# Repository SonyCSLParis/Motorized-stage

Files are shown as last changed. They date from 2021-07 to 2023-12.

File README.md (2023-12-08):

# CSL-stage
__keywords__: Stepper motors, Arduino, Python, Freecad, 3D printing

The goal of this module is to provide simple tools to control a motor to automate manual tasks.

An Arduino is used to control the stepper motors with motor shields. The motors are controllable: 
- via Arduino through the serial interface
- with a Python library that communicates serially with the Arduino
- with a user-friendly Tkinter interface based on the Python library
  
The use of limit-switches is integrated and is preferred for safety and reproducibility. 

## Pre-requisites

- Install [CSL-Serial](https://github.com/SonyCSLParis/CSL-Serial) and the [Arduino software](https://www.arduino.cc/en/software)
- The stepper motor(s) and motor shield(s) are readily available. Refer to the example gallery for ideas. 
- The code was tested on Windows and Linux

## Hardware :gear:
Check-out the example gallery and the description of how to implement them: turning a manual stage in a motorized one, building a microscope focus module, increasing the displacement range of a piezo-motor, etc. 

| Component|      Quantity      |  Price per unit | Example|  
|----------|:-------------:|------:|------:|  
| Arduino Uno |    1   |   24€ | [Robotshop](https://www.robotshop.com/eu/fr/microcontroleur-arduino-uno-r3-usb.html)|  
|Stepper motor | tested up to 3 | |
| Stepper driver | | |
| Wires | | |

## Software :desktop_computer:

| Software | Version we used | Download |
|----------|:-------------:|:-------------:|  
| Arduino | 1.8.13 | [download](https://www.arduino.cc/en/software)
| Python  | 3.7 |[install](https://github.com/Alienor134/Teaching/blob/master/Python/Installing_Anaconda_creating_environment.md)
| CSL-serial | 1.0 | [install](XXX)

## Codes and files provided :chart_with_upwards_trend:

An [Arduino code](Oquam/Oquam.ino) is provided to control the motors. An extra layer is added in Python to conntrol it easily.
[CSLstage](CSLstage/CSLstage.py) is a class that can be used the following way:

```python
from serial import Serial
from CSLstage import ControlStage

arduino_port = "COM6"

stage = ControlStage(arduino_port, [1,1,1]) #gearbox ratio of X, Y and Z axis
stage.handle_enable(1)
stage.move_dx(10)
stage.handle_enable(0)
stage.reset() 
```

# Instructions

## Connect the Arduino, the stepper driver and the stepper motor
Refer to the docmentation of the stepper driver you selected to perform the wiring. For example: [EasyDrive stepper motor driver](https://www.instructables.com/How-to-Interface-Easy-Driver-With-Stepper-Motor-Us/), [XY-motorized stage wiring](https://github.com/SonyCSLParis/Motorized-stage/tree/main/XY-stage), 

## Arduino and Python codes  

First install Arduino IDE and Python 3.7 (links in the **Software** section)  
Second download this repository. We will call the address where you save it "path/to/repo" (for example "C://User/Me/MyRepos").

Open the [Oquam/Oquam.ino](Oquam/Oquam.ino) file. 
Open it with Arduino IDE software by double clicking on the file **Oquam.ino** and upload the codes on the Arduino by clicking on the arrow. If it fails make sure that you are correctly connected to the Arduino: check the card type and the COM port in the "Tools" ("Outils" on the image). 

<p align="center">
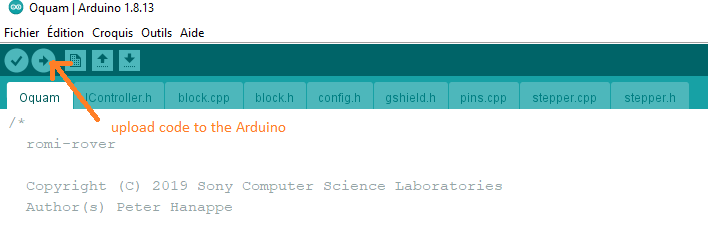
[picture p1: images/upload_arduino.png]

</p>

Note: You will have to determine the backlash of each of your motors: the number of steps you have to turn before the platform moves when you change directions. You will find 4 backlash values, one per direction per motor. We found backlash values between 7 and 12 steps. 

## Examples"

### Photos

    

### How to reproduce: 

https://github.com/SonyCSLParis/Motorized-stage/tree/main/XY-stage  
https://github.com/SonyCSLParis/Motorized-stage/tree/main/Z-stage  
https://github.com/openUC2/UC2-Motorized-XY-Table  

## License

This project is licensed under the [GNU General Public License v3.0](https://tldrlegal.com/license/gnu-general-public-license-v3-(gpl-3))

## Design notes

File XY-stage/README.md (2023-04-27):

# Automation of a manual microscope stage
__keywords__: Stepper motors, Arduino, Python, Freecad, 3D printing

The goal of this project is to convert a manual microscope stage into a motorized one.   
We control the motorized stage via Python and provide a user-friendly interface as well as the 3D models for the parts we replaced.
The precision of displacement approaches the micrometer.   
We added precisions for the budget. The maximum budget if you buy the manual stage and go through a supplier for the 3D-printing is 500€.

<p align="center">
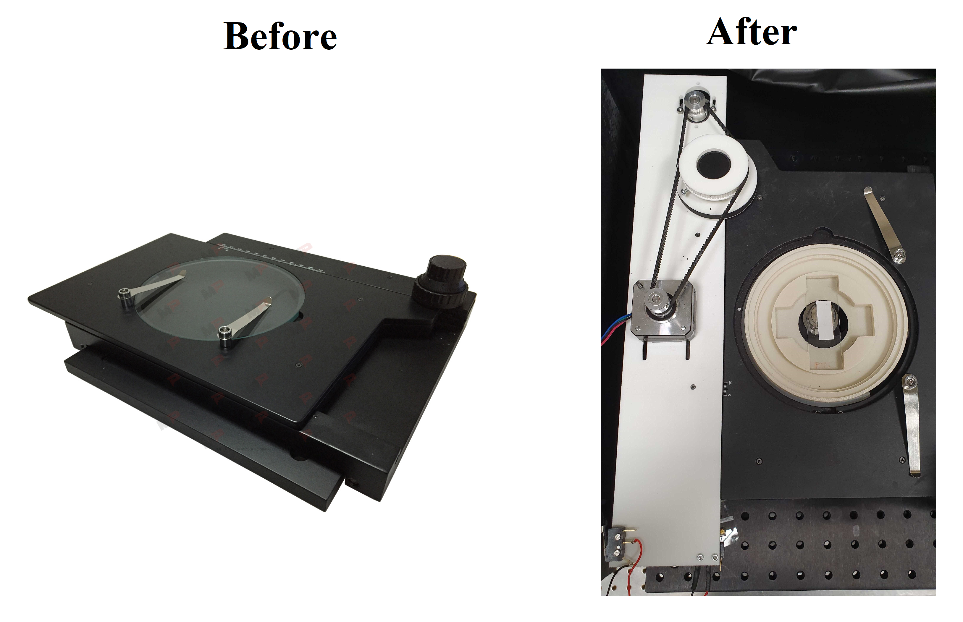
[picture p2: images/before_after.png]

</p>

# Method

The knobs initially used to manually move the platform are linked to motors via 2 belt-pulley systems (X and Y displacements). One removable part of the platform is replaced by a 3D-printed part that allows to fix the two motors. The pulleys are also 3D-printed to fit on the knobs. 

An Arduino is used to control the two stepper motors with two motor shields. The motors are controllable
-  via Arduino through the serial interface
- with a Python library that communicates serially with the Arduino
- with a user-friendly Tkinter interface based on the Python library

# Bill of materials

## Hardware :gear:
We used what we had in our drawers, it may be possible to reduce the costs by changing some of the equipment. 

| Component|      Quantity      |  Price per unit | Example|  
|----------|:-------------:|------:|------:|  
| Manual XY stage |  1 | 245€ | [Amazon](https://www.manualpositioning.com/e_products_show/?id=45)|  
| Arduino Uno |    1   |   24€ | [Robotshop](https://www.robotshop.com/eu/fr/microcontroleur-arduino-uno-r3-usb.html)|  
| Stepper driver | 2 |    10€ | [Robotshop](https://www.robotshop.com/eu/fr/controleur-moteur-pas-easydriver.html?gclid=EAIaIQobChMIhLiChaj58QIVxQwGAB1bUgYvEAQYASABEgIi8vD_BwE) |  
| Stepper motor  (0.9 °/s, 11 N/cm)  |1 | 11€ | [17HM08-1204S](https://www.omc-stepperonline.com/fr/nema-17-bipolaire-0-9deg-11ncm-15-6oz-in-1-2a-3-6v-42x42x21mm-4-fils.html)|  
| Stepper motor with gearbox| 1| 73€ |[42STH38-100](https://www.gotronic.fr/art-moteur-42sth38-100-18839.htm)|  
| Motor belt GT2 |2 |1€|[Phidgets](https://www.phidgets.com/?tier=2&catid=42&pcid=35) |
| Motor pulley 20 teeth/5mm bore |2 | 1€ |[Phidgets](https://www.phidgets.com/?tier=2&catid=42&pcid=35) | |
| Connection wires | | |  
| Screws M2, M3 | | |  
| 3D printer |

Websites where you can buy the hardware: Motedis, Phidgets, Robotshop, rs-online, RepRap

If you don't own a 3D printer you can use the platform [Sculpteo](https://www.sculpteo.com). Average delivery time: 2 weeks, possibility to pay for faster delivery. [Example of order](images/sculpteo_order.png).

## Software :desktop_computer:
Only open-source softwares

| Software | Version we used | Download |
|----------|:-------------:|:-------------:|  
| Freecad | 0.19 |  [download](https://wiki.freecadweb.org/Download)
| Arduino | 1.8.13 | [download](https://www.arduino.cc/en/software)
| Python  | 3.7 |[install](https://github.com/Alienor134/Teaching/blob/master/Python/Installing_Anaconda_creating_environment.md)

## Codes and files provided :chart_with_upwards_trend:

### 3D designs: 
- [scalable pulley Freecad](3D_models/large_button.FCStd) (modified from [manueaswn's scalable pulley](https://www.thingiverse.com/thing:3875983) )
- [small button pulley](3D_models/large_button_100t.stl)  
- [large button pulley](3D_models/medium_button_80t.stl)
- [plate element](3D_models/plaque_moteur_gearbox.stl)

### Control of motors by Arduino 
- [libromi](https://github.com/romi/libromi/tree/c6992f0516e695cd28e09cd8dcbb921d4bc2097d) (written for the [Romi Project](https://github.com/romi/libromi))
- [interface](codes/launch_interface.py)

# Results

In the end we were able to control the movement of the stage to go from one trap to the following one. The following animation shows a trap and its neighbour appearing one after the other in the center of the camera.

<p align="center">

</p>

<p align="center">
Credits: Léa Pinon and Jacques Fattacioli for the microfluidic set-up (ENS, IPGG), Thomas Le Saux and Aliénor Lahlou for the imaging set-up (ENS, Sony CSL)
</p>  

By using the EasyDriver we could rotate each motor by one microstep. In the end the set-up enabled us to reach a minimal movement of 1,95 μm along the **x** axis and of 0,05 μm along the **y** axis.

In order to estimate the quality of our set-up, we measured its precision using the registration method which calculates the spatial correlation between two successive images.

On the one hand the analyses of these results shows that the stage moves linearly along the **y** axis as expected. We concluded that our set-up was of good quality for this direction.

<p align="center">
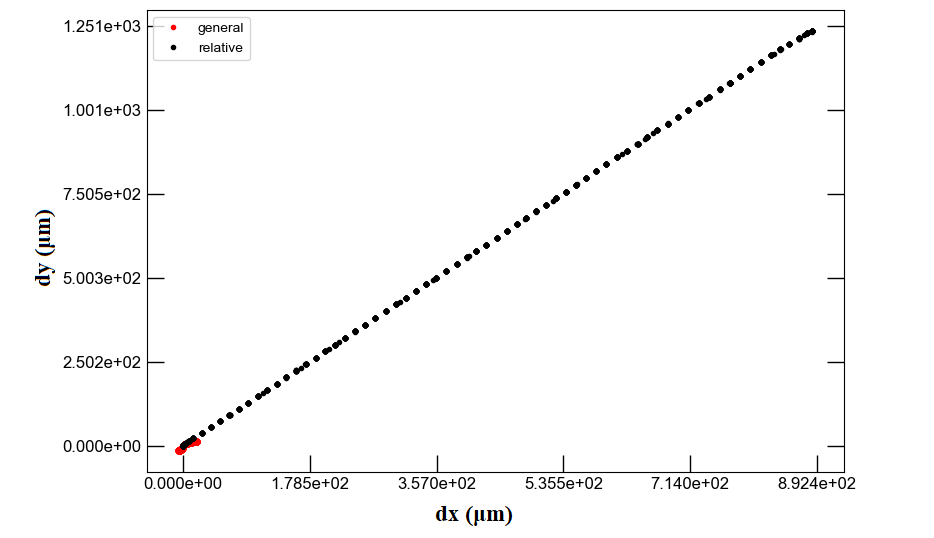
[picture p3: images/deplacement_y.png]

</p>

On the other hand we discovered that the movement along the **x** axis is flawed. Indeed when moving the stage along this axis we regularly measure a small unwanted movement along the **y** axis. This shortcoming leads to imprecise movement along the **x** axis, and it seems to come from the mechanics of the manual platform.

<p align="center">
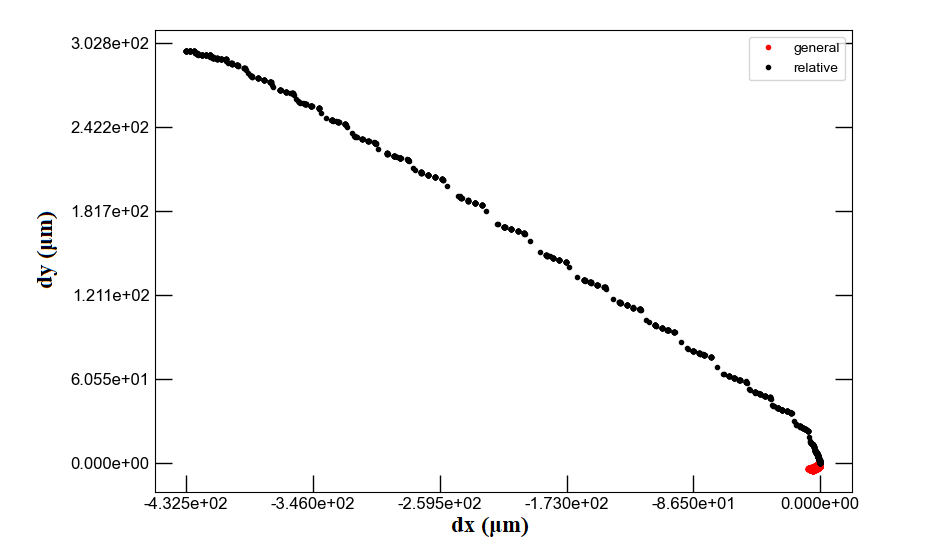
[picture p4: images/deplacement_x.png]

</p>

For the **x**-axis we measured that one turn of the knob moves the stage by 2,5 cm. In the case of the **x** axis the 17HM08-1204S stepper motor has 3200 microsteps per revolution and the master pulley has 20 teeth. Thus we calculated that the **x**-axis slave pulley needed to have 32 teeth. Such a little number of teeth leads to modeling issues.

Thus we decided to design an 80 teeth slave pulley for the **x**-axis knob. This leads to a higher precision : when the stepper motor rotates by 1 microstep, the stage moves by 1,95 μm along the **x** axis (with a simple Nema 17 motor)

### New plate

Because of structural constraints, the stepper motors had to be fixed to the stage. This is why we decided to replace a plate screwed upon the stage by a new one whose 3D template we created by using FreeCAD.

This new plate has attachment points for both stepper motors and for potential switches and can be screwed to the stage.

<p align="center">
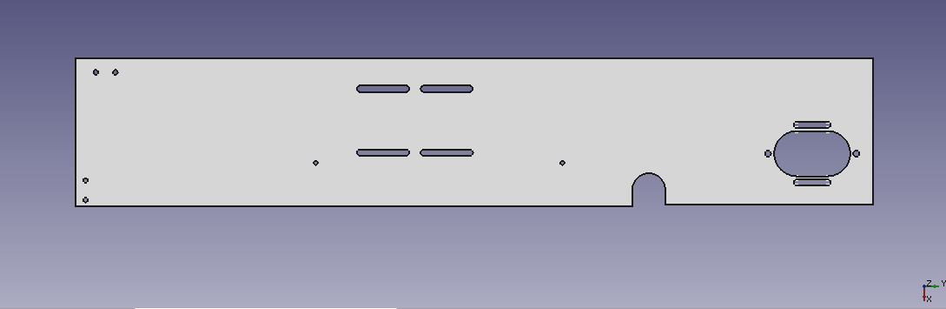
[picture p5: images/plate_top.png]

</p>  

## Assembly

In order to keep things simple we decided to control both stepper motors with one Arduino UNO microcontroller. We still had to use one EasyDriver microcontroller for each stepper motor. We used [Brian Schmalzhaus' example](https://www.schmalzhaus.com/EasyDriver/Examples/EasyDriverExamples.html) running multiple stepper motors. The set-up can be seen in the following diagram. As we wanted precise movements, we enabled microstepping control for both motors by adding connections between the MS1 and MS2 pins and the ground for each EasyDriver microcontroller.

<p align="center">
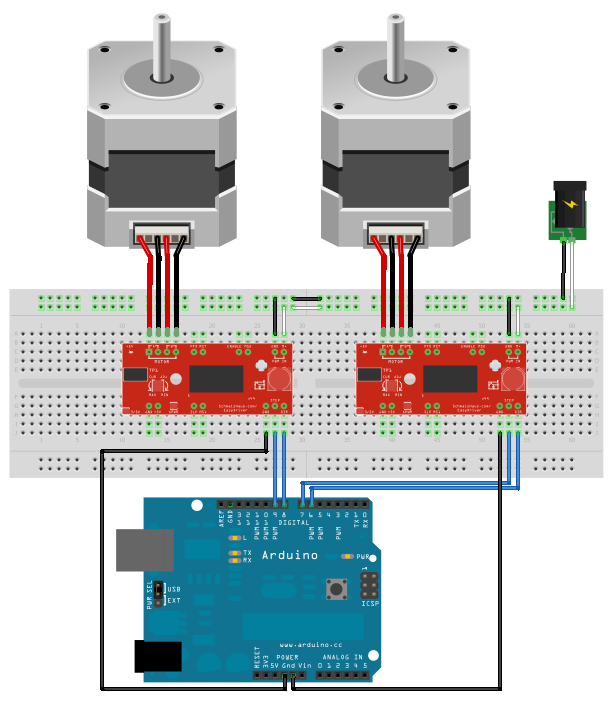
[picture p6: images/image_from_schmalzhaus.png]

</p>

To make the interaction user-friendly, we developed a code that sends instructions to the Arduino through the Serial port. It requires Python. If you already use Python for other projects, you will want to keep this code isolated from your current install. This is possible with a virtual environment. Open Anaconda Prompt and navigate to the repository

```
conda env create -f environment.yml
```
Now activate the environment:  

```
conda activate motorized-stage
``` 

You can launch the interface 

```
cd path/to/repo (here replace by your own path)
cd XY-stage/codes
python launch_interface.py
```
Press the buttons to move by predefined values, or enter manually a value and press the "move" button. The values correspond to motor steps.

<p align="center">
<img src="../images/command_interface.png" width=400"/>
</p>

Note: You will have to determine the backlash of each of your motors: the number of steps you have to turn before the platform moves when you change directions. You will find 4 backlash values, one per direction per motor. We found backlash values between 7 and 12 steps. 

## Thanks

We thank Peter Hanappe for the advices on the mechanical parts and for providing codes to control the motors. We thank Eric Aït-Yahiatène for the 3D-printing. 

## License

This project is licensed under the [GNU General Public License v3.0](https://tldrlegal.com/license/gnu-general-public-license-v3-(gpl-3))

## Contacts
If you have questions you can contact Ali Ruyer-Thompson (ali.ruyer--thompson :email: ens.psl.eu) or Aliénor Lahlou (alienor.lahlou :email: ens.psl.eu)

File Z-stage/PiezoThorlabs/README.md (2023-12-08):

# Coarse control of a piezo-controlled translation stage

Thorlabs provides a travel stage ([NFL5DP20](https://www.thorlabs.com/newgrouppage9.cfm?objectgroup_id=720&pn=NFL5DP20/M)) with a coarse manual translation range of 5 mm with possibility to 
actuate a fine transational movement with a piezo controller ([KPZ101](https://github.com/SonyCSLParis/Motorized-stage/blob/main/Z-stage/PiezoThorlabs/KPZ101.jpg)).  

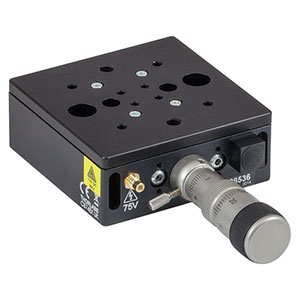
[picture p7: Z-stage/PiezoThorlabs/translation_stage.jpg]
stage

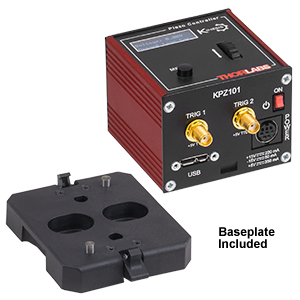
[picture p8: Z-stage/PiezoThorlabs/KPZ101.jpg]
piezo
  

The Thorabs translation stage translation movement controlled by a piezoelectric controller allows fine movements that could not be achieved with a stepper motor. However, the automated range of displacement of the stage is intrisically limited by the piezo, to 20 µm.   
We decided to automate the coarse control with a stepper motor connected to the manual differential micrometer drive via a belt-pulley system. the pulley was designed using the parametric pulley model provided [here](). We added holes to attach the piece to the differential drive part with screws.  

The part we designed has 55 teeth and can be found [here](https://github.com/SonyCSLParis/Motorized-stage/blob/main/Z-stage/PiezoThorlabs/z_focus_55_teeth_190.stl).  

setup

The design requires to adjust the position of the motor pulley to keep the belt orthogonal to the drive rotation, and to firmly attach the stepper motor to the optcal bed.   

The Nema motor is controlled by CSL-stage code, according to the descripition here: https://github.com/SonyCSLParis/Motorized-stage.

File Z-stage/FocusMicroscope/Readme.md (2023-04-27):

# 3D design for the autofocus component

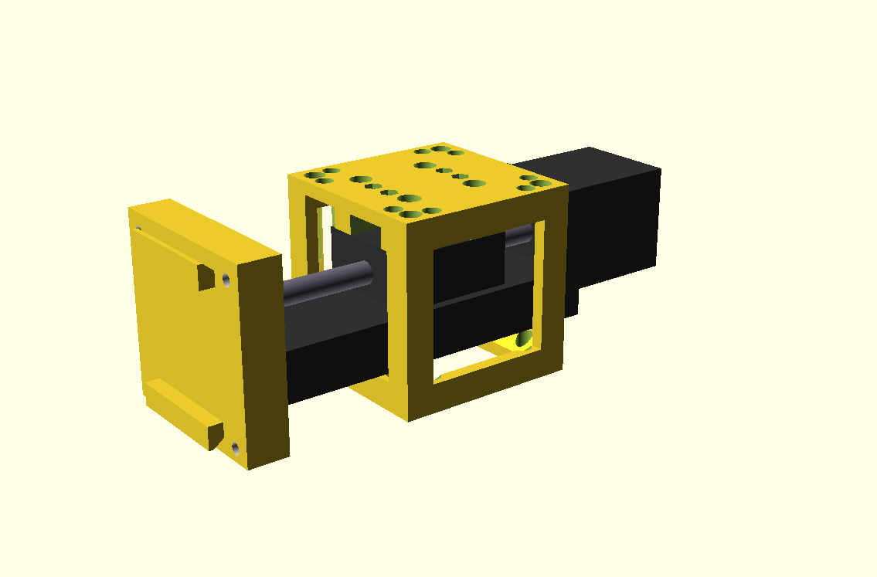
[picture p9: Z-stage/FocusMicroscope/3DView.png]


The autofocus module is based on the small linear slider found, among other, on Amazon ([French site](https://www.amazon.fr/dp/B08Y6VZMC8?ref=ppx_yo2ov_dt_b_product_details&th=1), [US site](https://www.amazon.com/s?k=Linear+Rail+50mm+nema11&crid=AHAYTX9E18IR&sprefix=linear+rail+50mm+nema%2Caps%2C635&ref=nb_sb_noss)).

On the front side, the sample holder snaps onto the front panel of the slider thanks to four spheric magnets. The sample itself is held using a simple rubber band.

The module includes two limit switches to detect the start and end position of the linear slider. The switches are the [Omron D2F-01L-D3](https://omronfs.omron.com/en_US/ecb/products/pdf/en-d2f.pdf).

The current 3D design was made with [OpenScad](https://openscad.org/).

The main files are:

* FocusMicroscope.scad: The main file that bundles the different components together.
* Structure.scad: The components of the focus module.
* LinearSlider.scad: 3D model of the linear slider.
* UC2.scad: A 3D model of the UC2 cube.

## Bill of materials

| Quantity | Description |
|----------|-------------|
| 1 | [Linear slider](https://www.amazon.com/s?k=Linear+Rail+50mm+nema11&crid=AHAYTX9E18IR&sprefix=linear+rail+50mm+nema%2Caps%2C635&ref=nb_sb_noss) (50 mm or 100 mm, NEMA11 stepper motor) |
| 2 | M2 x xx mm screws  |
| 2 | M2 nuts |
| 4 | M3 x xx mm screws |
| 2 | M3 x xx mm screws |
| 4 | Spheric magnets, 5 mm |
| 2 | [Omron D2F-01L-D3](https://omronfs.omron.com/en_US/ecb/products/pdf/en-d2f.pdf) |
| - | Wire for the limit switches |

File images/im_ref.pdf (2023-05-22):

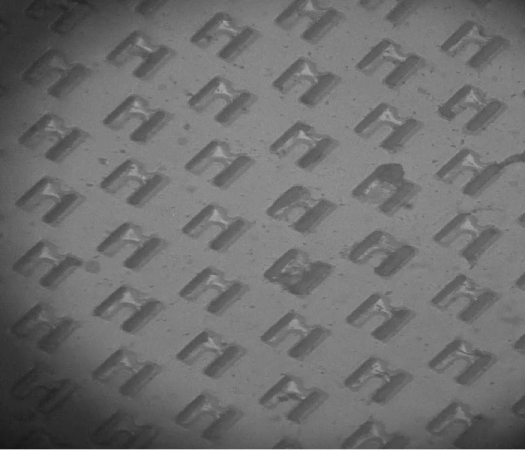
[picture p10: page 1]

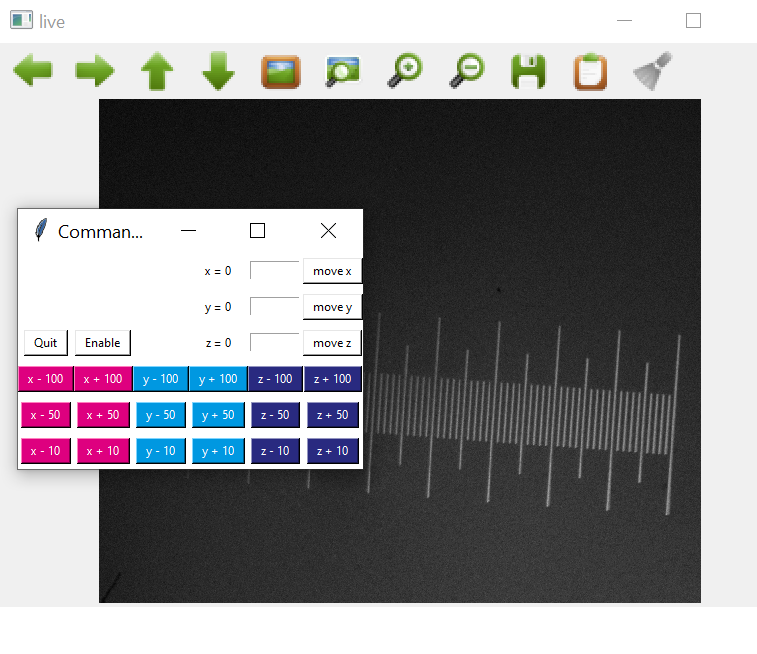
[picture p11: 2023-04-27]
images/inter_xyz.png

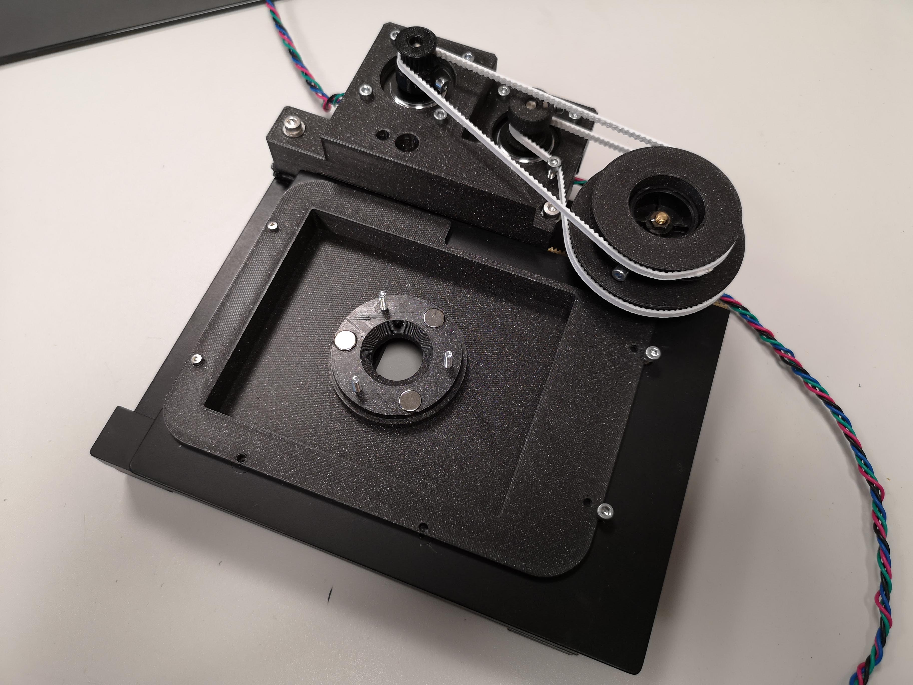
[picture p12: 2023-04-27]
images/UC2_stage.jpg

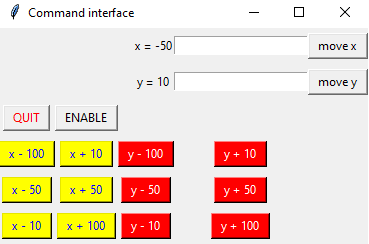
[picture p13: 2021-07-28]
images/command_interface.png

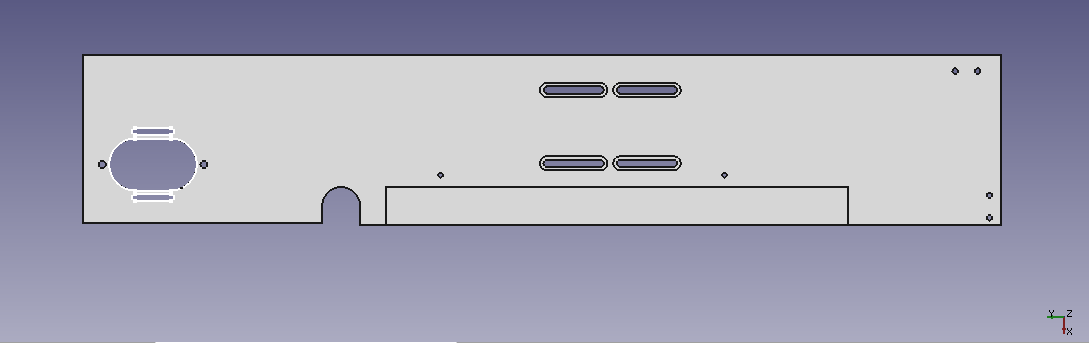
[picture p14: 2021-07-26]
images/plate_bottom.png

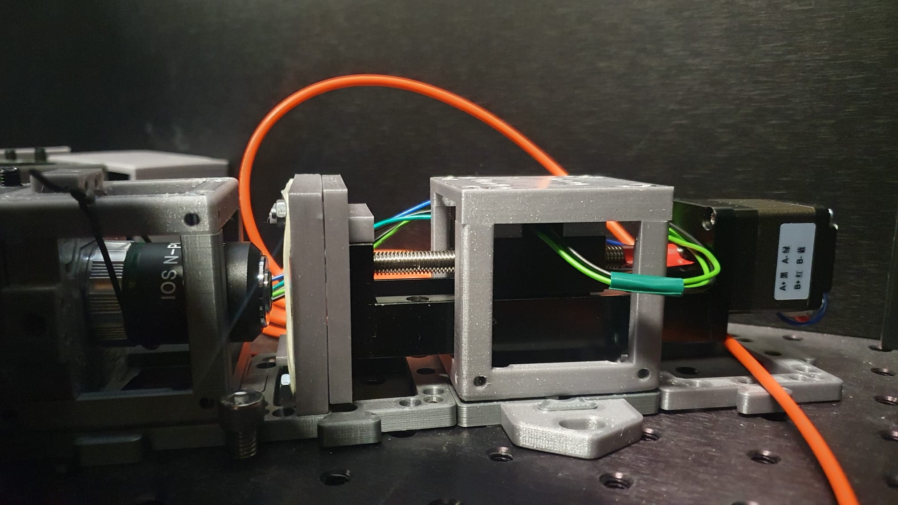
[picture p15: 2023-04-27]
images/Z_focus_UC2.jpg

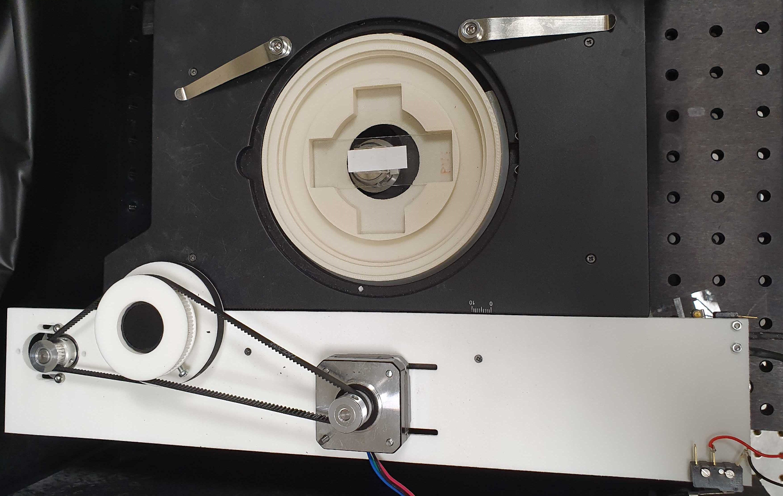
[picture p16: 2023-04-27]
images/modified_stage.jpg

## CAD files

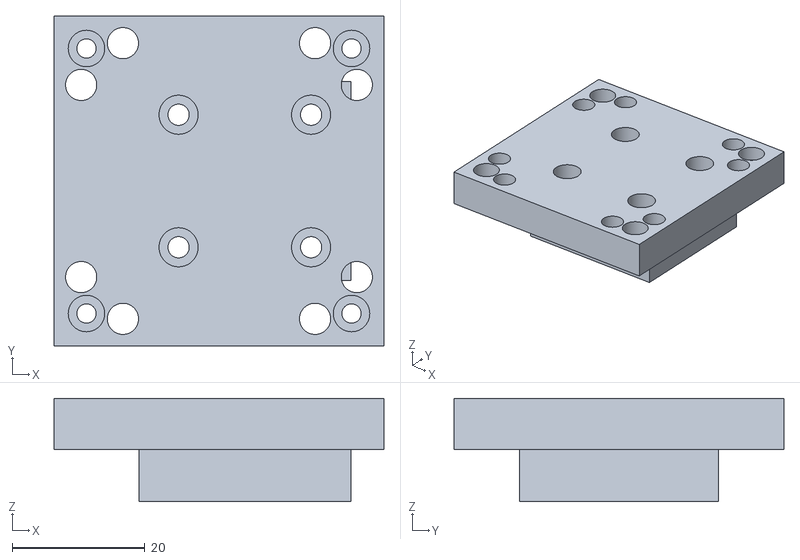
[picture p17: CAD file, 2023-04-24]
XY-stage/3D_models/FocusMicroscope_Top.stl
49.8 x 49.8 x 15.6

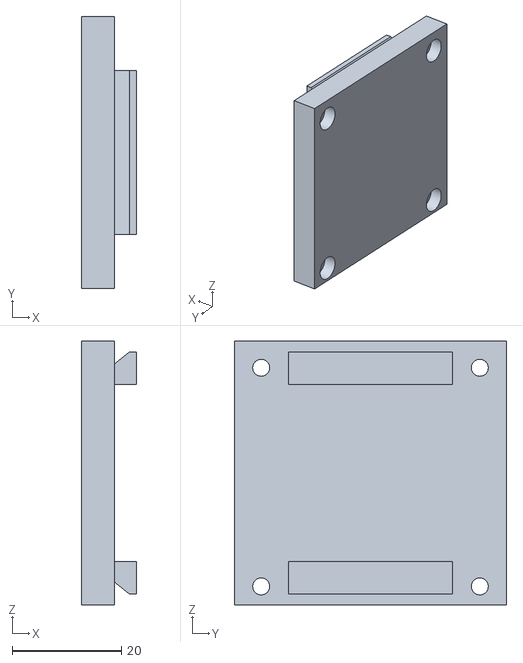
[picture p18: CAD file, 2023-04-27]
Z-stage/FocusMicroscope/SampleHolder.stl
10.0 x 49.8 x 48.3

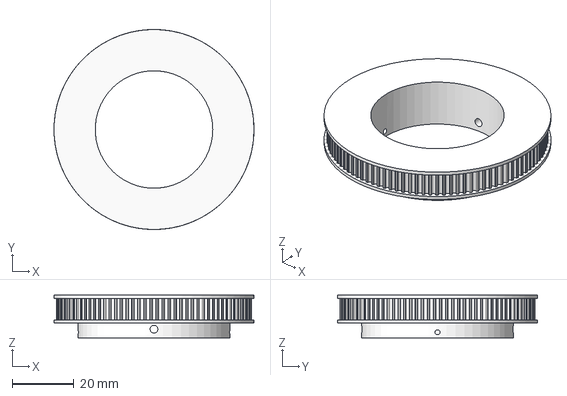
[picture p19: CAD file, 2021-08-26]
XY-stage/3D_models/large_button.FCStd
64.7 x 64.7 x 13.8 mm

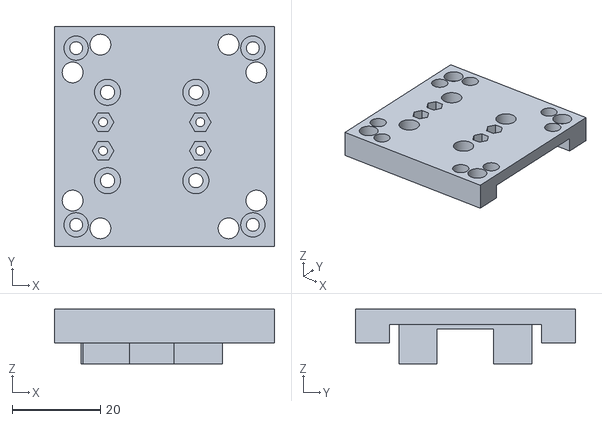
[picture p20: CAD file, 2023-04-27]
Z-stage/FocusMicroscope/StructureTop.stl
49.8 x 49.8 x 12.4

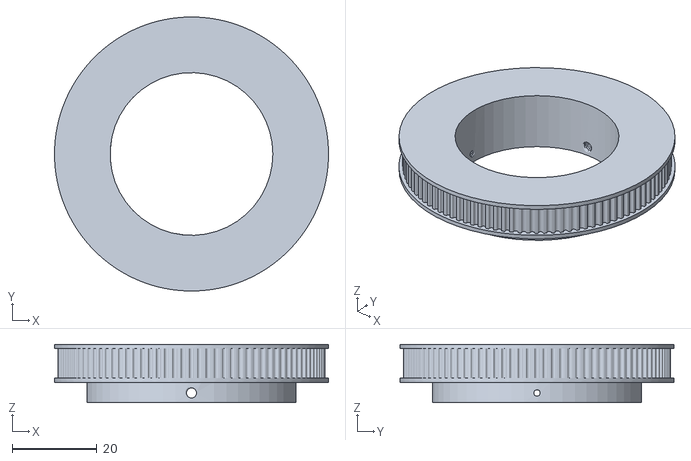
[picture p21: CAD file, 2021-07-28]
XY-stage/3D_models/large_button_100t.stl
64.7 x 64.7 x 13.8

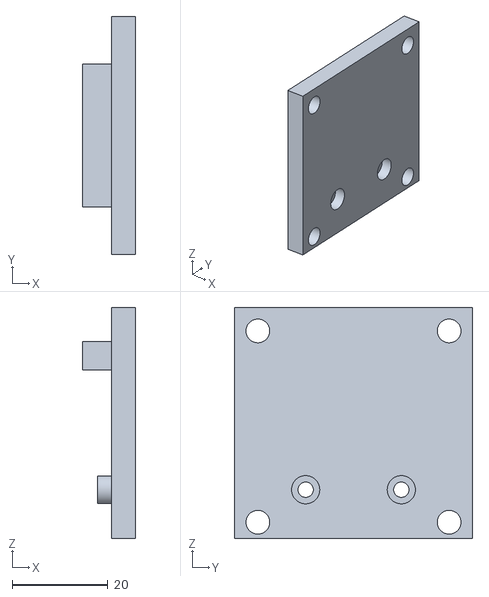
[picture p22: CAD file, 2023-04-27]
Z-stage/FocusMicroscope/FrontPanel.stl
11.1 x 49.8 x 48.3

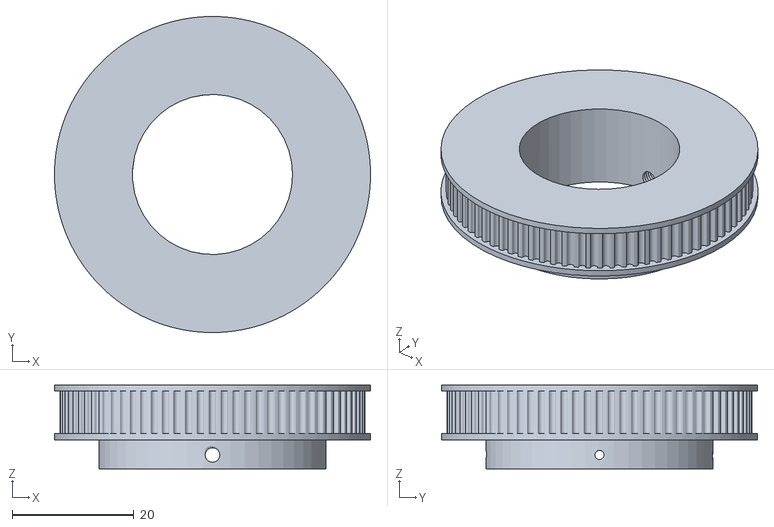
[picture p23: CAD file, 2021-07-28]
XY-stage/3D_models/medium_button_80t.stl
51.9 x 51.9 x 13.8

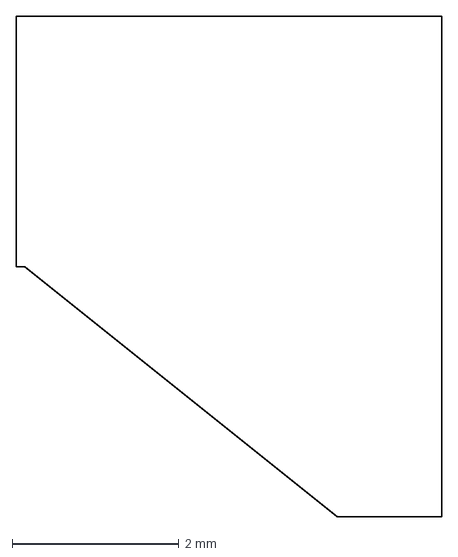
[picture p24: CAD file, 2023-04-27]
Z-stage/FocusMicroscope/SampleHolderRail.dxf
5.10 x 6.00 mm

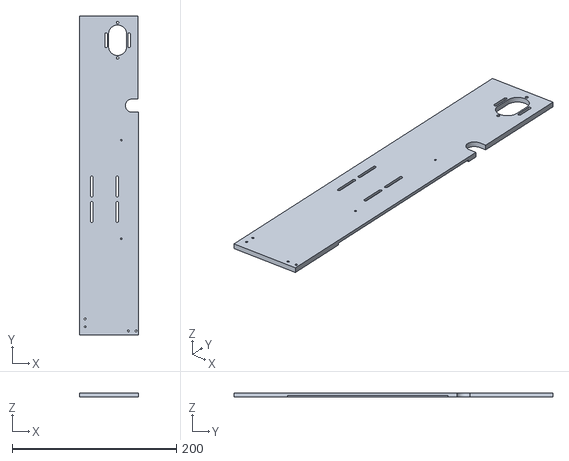
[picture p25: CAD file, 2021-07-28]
XY-stage/3D_models/plaque_moteur_gearbox.stl
72.0 x 388.0 x 5.00

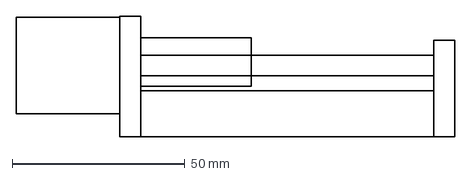
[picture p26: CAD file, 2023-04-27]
Z-stage/FocusMicroscope/LinearSlider.dxf
127.0 x 35.0 mm

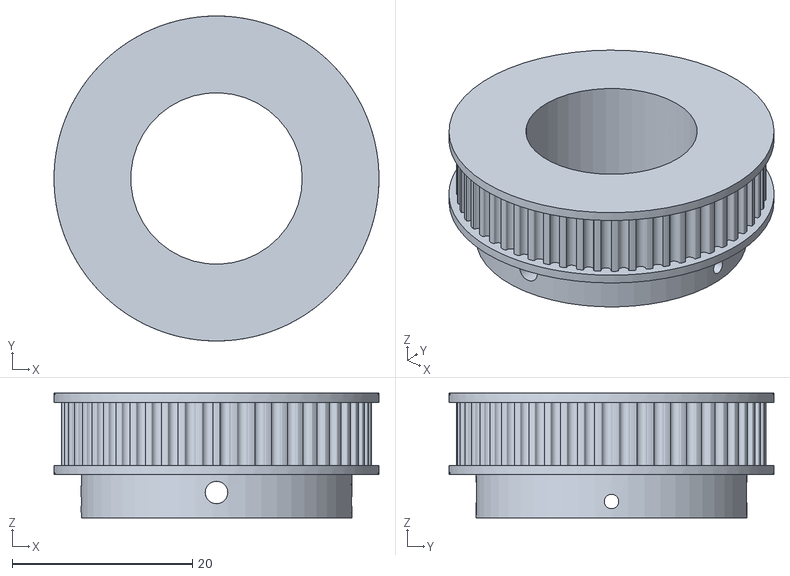
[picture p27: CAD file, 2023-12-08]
Z-stage/PiezoThorlabs/z_focus_55_teeth_190.stl
36.0 x 36.0 x 13.8

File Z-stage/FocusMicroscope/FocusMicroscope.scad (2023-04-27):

include <units.scad>
include <LinearSlider.scad>
include <Structure.scad>

// X-position of the slider
// Note: The 3D model moves along the x-axis, but in the Arduino 
// code it moves along the z-axis.
x = 20;

slider_x = kUC2CubeSize - kFrontPlateDepth - kSliderLength - x;
slider_y = kUC2CubeSize/2;
slider_z = -kSliderOffsetAxis + kUC2CubeSize - computeSocketHeight();


UC2CubeBottom();
translate([kUC2CubeSize, kUC2CubeSize, kUC2CubeSize]) {
    rotate([0, 0, 180]) // FIXME
        StructureTop();
}

translate([slider_x, 0, 0]) {
    translate([0, slider_y, slider_z]) 
        LinearSlider(x);
    translate([kDistancePlates + kFrontPlateDepth, 0, 0])
        FrontPanel();
    translate([kDistancePlates + kFrontPlateDepth + kFrontPanelDepth, 0, 0])
        SampleHolder();
}

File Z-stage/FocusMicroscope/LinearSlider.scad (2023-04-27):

include <materials.scad>
include <units.scad>

// Expected kLength: 85 + 6 + 6 + 30 = 127 mm
// Measured kLength: 127.25 mm
kLength = 127*mm;
kWidth = 30*mm;
kHeight = 35*mm;

kMotorLength = 30*mm;
kMotorWidth = 28*mm;
kMotorHeight = 28*mm;

kMotorPlateDepth = 6*mm;
kMotorPlateWidth = kWidth;
kMotorPlateHeight = kHeight;

kFrontPlateDepth = 6*mm;
kFrontPlateWidth = kWidth;
kFrontPlateHeight = 28*mm;
kFrontPlateScrewHeadDiameter = 5.8*mm;
kFrontPlateScrewHeadOffset = 0.1*mm;
kFrontPlateScrewDistance = 20*mm;

kDistancePlates = kLength - kMotorLength - kFrontPlateDepth - kMotorPlateDepth;
kAxisLength = kDistancePlates + kFrontPlateDepth + kMotorPlateDepth;
kAxisDiameter = 6*mm;

kOffsetMotorAndMotorPlate = 0.3*mm;
kOffsetBottom = -kMotorPlateHeight + kMotorHeight/2 + kOffsetMotorAndMotorPlate;

kBottomLength = kDistancePlates;
kBottomWidth = kWidth;
kBottomHeight = 13.42*mm;

kSliderLength = 32*mm;
kSliderWidth = kWidth;
kSliderHeight = 14*mm;
kSliderDistanceHoles = 20*mm;
kSliderHoleDiameter = 5*mm;
kSliderOffsetAxis = 8*mm;

module Motor()
{
    color(BlackPaint)
    translate([-kMotorLength, -kMotorWidth/2, -kMotorHeight/2]) {
        cube([kMotorLength, kMotorWidth, kMotorHeight]);
    }
}

module MotorPlate()
{
    color(BlackPaint) {
        translate([-kMotorPlateDepth, 
                   -kMotorPlateWidth/2, 
                   kOffsetBottom]) {
                cube([kMotorPlateDepth, kMotorPlateWidth, kMotorPlateHeight]);
        }
    }
}

module FrontPlate()
{        
    color(BlackPaint) {
        translate([kDistancePlates, 0, 0])
        difference() {
            translate([0, -kFrontPlateWidth/2, kOffsetBottom]) {
                    cube([kFrontPlateDepth, kFrontPlateWidth, kFrontPlateHeight]);
            }
            translate([kFrontPlateDepth + epsilon, 0, 0]) {
                rotate([0, -90, 0]) {
                    cylinder(d = kAxisDiameter + epsilon,
                             h = kFrontPlateDepth + 2 * epsilon, $fn=360);
                }
            }
        }
    }
}

module Axis()
{
        color(Stainless) {
            translate([-kMotorPlateDepth, 0, 0])
            rotate([0, 90, 0])
                cylinder(d = kAxisDiameter, h = kAxisLength, $fn=360);
        }
}

module Bottom()
{
    color(BlackPaint) {
        translate([0, -kBottomWidth/2, kOffsetBottom]) {
            cube([kBottomLength, kBottomWidth, kBottomHeight]);
        }
    }
}

module Slider()
{
    color(BlackPaint) {
        translate([kSliderLength/2, 0, -(kSliderHeight - kSliderOffsetAxis)]) 
        difference() {
            translate([-kSliderLength/2, -kSliderWidth/2, 0]) {
                cube([kSliderLength, kSliderWidth, kSliderHeight]);
            }
            translate([kSliderDistanceHoles/2, kSliderDistanceHoles/2, -epsilon]) {
                cylinder(d = kSliderHoleDiameter, 
                         h = kSliderHeight + 2 * epsilon, $fn=360);
            }
            translate([kSliderDistanceHoles/2, -kSliderDistanceHoles/2, -epsilon]) {
                cylinder(d = kSliderHoleDiameter, 
                         h = kSliderHeight + 2 * epsilon, $fn=360);
            }
            translate([-kSliderDistanceHoles/2, kSliderDistanceHoles/2, -epsilon]) {
                cylinder(d = kSliderHoleDiameter, 
                         h = kSliderHeight + 2 * epsilon, $fn=360);
            }
            translate([-kSliderDistanceHoles/2, -kSliderDistanceHoles/2, -epsilon]) {
                cylinder(d = kSliderHoleDiameter, 
                         h = kSliderHeight + 2 * epsilon, $fn=360);
            }
        }
    }
}

module LinearSlider(pos)
{
    translate([-kMotorPlateDepth, 0, 0])
        Motor();
    
    translate([0, 0, 0])
        MotorPlate();

    translate([0, 0, 0])
        FrontPlate();
 
    translate([0, 0, 0])
        Axis();

    translate([0, 0, 0])
        Bottom();

    pos_min = 0;
    pos_max = kDistancePlates - kSliderLength;
    x = max(pos_min, min(pos_max, pos));

    translate([x*mm, 0, 0])
        Slider();
}

//LinearSlider(0);

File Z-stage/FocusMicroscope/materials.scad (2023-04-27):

/*
 * Material colors.
 * 
 * Originally by Hans Häggström, 2010.
 * Dual licenced under Creative Commons Attribution-Share Alike 3.0 and LGPL2 or later
 */

// Material colors
Oak = [0.65, 0.5, 0.4];
Pine = [0.85, 0.7, 0.45];
Birch = [0.9, 0.8, 0.6];
FiberBoard = [0.7, 0.67, 0.6];
BlackPaint = [0.2, 0.2, 0.2];
Iron = [0.36, 0.33, 0.33];
Steel = [0.65, 0.67, 0.72];
Stainless = [0.45, 0.43, 0.5];
Aluminum = [0.77, 0.77, 0.8];
Brass = [0.88, 0.78, 0.5];
Transparent = [1, 1, 1, 0.2];

// Example, uncomment to view
//color_demo();

module color_demo(){
    // Wood
    colorTest(Oak, 0, 0);
    colorTest(Pine, 1, 0);
    colorTest(Birch, 2, 0);

    // Metals
    colorTest(Iron, 0, 1);
    colorTest(Steel, 1, 1);
    colorTest(Stainless, 2, 1);
    colorTest(Aluminum, 3, 1);

    // Mixboards
    colorTest(FiberBoard, 0, 2);

    // Paints
    colorTest(BlackPaint, 0, 3);
}

module colorTest(col, row=0, c=0) {
  color(col) translate([row * 30,c*30,0]) sphere(r=10);
}

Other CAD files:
Z-stage/FocusMicroscope/screws.scad
Z-stage/FocusMicroscope/Structure.scad
Z-stage/FocusMicroscope/UC2.scad
Z-stage/FocusMicroscope/units.scad

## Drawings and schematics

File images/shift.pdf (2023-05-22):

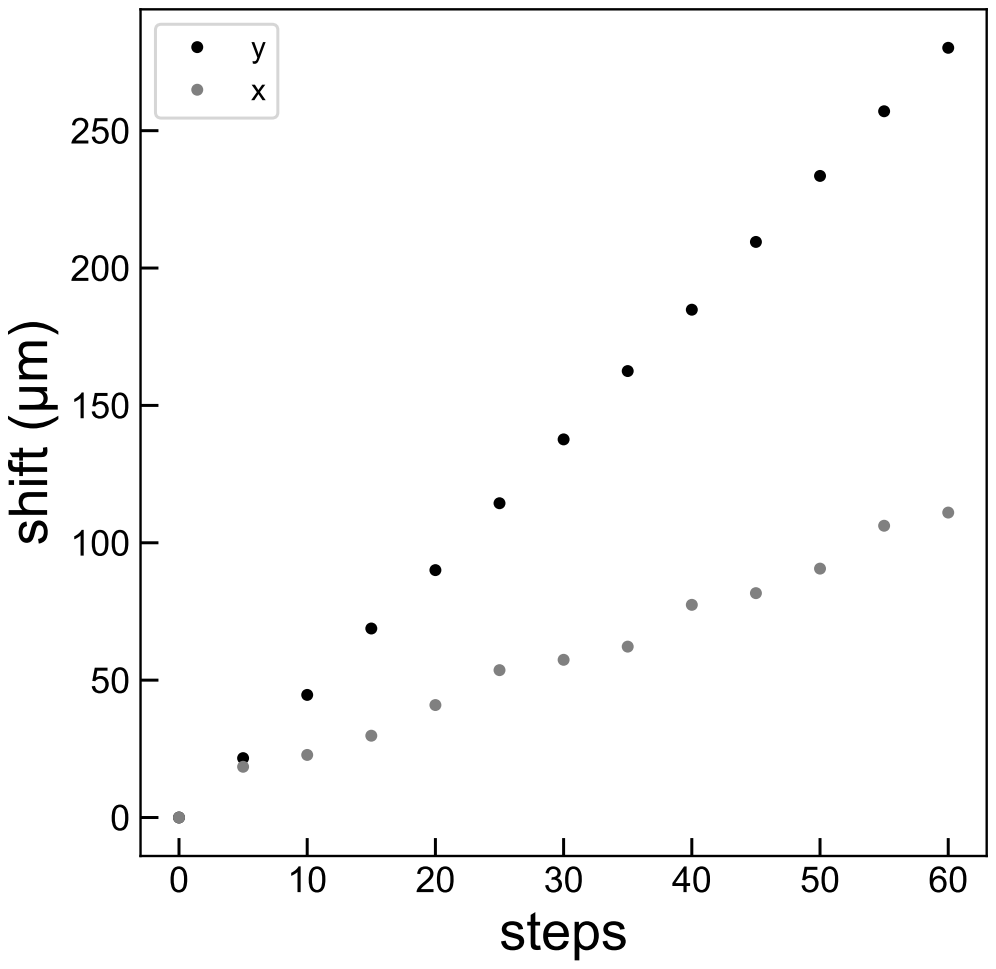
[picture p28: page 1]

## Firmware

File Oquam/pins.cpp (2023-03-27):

/*
  romi-rover

  Copyright (C) 2019 Sony Computer Science Laboratories
  Author(s) Peter Hanappe

  romi-rover is collection of applications for the Romi Rover.

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
  You should have received a copy of the GNU General Public License
  along with this program.  If not, see
  <http://www.gnu.org/licenses/>.

 */
#include "Arduino.h"
#include "config.h"

/**
 * \brief Configure the step and dir pins as output.
 */
void init_pins() 
{
        /* Enable output on the selected pins */
        STEP_DDR |= STEP_MASK;
        DIRECTION_DDR |= DIRECTION_MASK;
        STEPPERS_DISABLE_DDR |= STEPPERS_DISABLE_MASK;
        
        // Set as input pins and enable internal pull-up
        // resistors. Normal high operation
        pinMode(PIN_LIMIT_SWITCH_X, INPUT_PULLUP);  
        pinMode(PIN_LIMIT_SWITCH_Y, INPUT_PULLUP);  
        pinMode(PIN_LIMIT_SWITCH_Z, INPUT_PULLUP);  

        // Set as output pins
        pinMode(PIN_SPINLDE, OUTPUT);  
        digitalWrite(PIN_SPINLDE, LOW);
}

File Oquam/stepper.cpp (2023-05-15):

/*
  romi-rover

  Copyright (C) 2019 Sony Computer Science Laboratories
  Author(s) Peter Hanappe

  romi-rover is collection of applications for the Romi Rover.

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
  You should have received a copy of the GNU General Public License
  along with this program.  If not, see
  <http://www.gnu.org/licenses/>.

 */
// CPU frequency Uno: 16000000
// Timer 1: Stepper timer
// Timer 2: Reset step pins

#include "Arduino.h"
#include "config.h"
#include "block.h"
#include "stepper.h"

volatile int32_t stepper_position_[3];
volatile int32_t accumulation_error_[3];
volatile int32_t delta_[3];
volatile int32_t dt_;
volatile int16_t step_dir_[3];
//volatile int32_t counter_reset_timer = 0;
volatile block_t *current_block_;
volatile int32_t interrupts_ = 0;
volatile int16_t milliseconds_ = 0;
volatile int8_t stepper_reset_ = 0;

void stepper_zero()
{
        for (int i = 0; i < 3; i++) {
                stepper_position_[i] = 0;
                accumulation_error_[i] = 0;
        }
}

void stepper_reset()
{
        stepper_reset_ = 1;
}

void init_stepper()
{
        stepper_zero();
        cli();
        init_stepper_timer();
        init_reset_step_pins_timer();
        sei(); 
}

void get_stepper_position(int32_t *pos)
{
        pos[0] = stepper_position_[0];
        pos[1] = stepper_position_[1];
        pos[2] = stepper_position_[2];
}

bool stepper_is_idle()
{
        return ((block_buffer_available() == 0)
                && (current_block_ == 0));
}

/*
 
  https://fr.wikiversity.org/wiki/Micro_contr%C3%B4leurs_AVR/Le_Timer_1
  http://maxembedded.com/2011/07/avr-timers-ctc-mode/
  

 */
/**
 * \brief: Initialize Timer2 to reset the STEP pins back to zero 10 µs
 * after a pulse.
 *
 *  Timer2 is used as the "reset step timer", i.e. this timer will
 *  pulse the set the STEP pins of the stepper drivers to zero 10 µs
 *  after they have been raised to 1 by the stepper timer.
 */
void init_reset_step_pins_timer()
{
        /* Don't enable the timer, yet. */
        TIMSK2 &= ~(1 << OCIE2A);

        // Use the waveform generation mode, or Clear Timer on Compare
        // (CTC) mode:
        //
        // Register  WGM22 WGM21 WGM20
        // TCCR2A          1     0
        // TCCR2B    0                 
        TCCR2A &= ~(1 << WGM20);
        TCCR2A |=  (1 << WGM21);
        TCCR2B &= ~(1 << WGM22); 

        // Disconnect OC1 output: Don't send the PWM to an output
        // pin.
        TCCR2A &= ~((1 << COM2A1) | (1 << COM2A0)
                    | (1 << COM2B1) | (1 << COM2B0));

        // Set the prescaling
        //   CS22  CS21  CS20
        //   0     0     0     Disabled
        //   0     0     1     1
        //   0     1     0     8
        //   0     1     1     32
        //   1     0     0     64
        //   1     0     1     128
        //   1     1     0     256
        //   1     1     1     1024

        // Prescaling: 8
        TCCR2B &= ~(1 << CS20);
        TCCR2B |=  (1 << CS21);
        TCCR2B &= ~(1 << CS22);
        // TCCR2B &= ~(1 << CS20);
        // TCCR2B &= ~(1 << CS21);
        // TCCR2B &= ~(1 << CS22);

        /* Set the compare value:

           Timer delay = T = 10 µs
           F_CPU = 16 MHz
           Prescaling = 8
           F_CLOCK = 2 MHz
           P_CLOCK = 1/2 µs
           N = 10 µs / (1/2 µs) = 20
           N-1 = 19
           
           int n = T / (1 / F_CPU / prescaling) - 1
                 = (T * F_CPU / prescaling) - 1
                 = 19
        */
        OCR2A = 19;
        
        /* Initialize counter */
        TCNT2 = 0;
}

/**
 * \brief: Configure Timer1 to drive the stepper's STEP pulse train.
 *
 *  Timer1 is used as the "stepper timer", i.e. this timer will pulse
 *  the STEP pins of the stepper drivers.
 */
void init_stepper_timer()
{
        current_block_ = 0;

        /* Don't enable the timer, yet */
        TIMSK1 &= ~(1 << OCIE1A);
        
        // Use the waveform generation mode, or Clear Timer on Compare
        // (CTC) mode.
        //
        // Register  WGM13 WGM12 WGM11 WGM10  
        // TCCR1A                0     0    
        // TCCR1B    0     1                
        TCCR1A &= ~(1 << WGM10);
        TCCR1A &= ~(1 << WGM11);
        TCCR1B |=  (1 << WGM12);
        TCCR1B &= ~(1 << WGM13); 

        // Disconnect OC1 output: Don't send the PWM to an output
        // pin.
        TCCR1A &= ~((1 << COM1A1) | (1 << COM1A0)
                    | (1 << COM1B1) | (1 << COM1B0));
        
        // Set the prescaling
        //   CS12  CS11  CS10
        //   0     0     0     Disabled
        //   0     0     1     1
        //   0     1     0     8
        //   0     1     1     64
        //   1     0     0     256
        //   1     0     1     1024
        //   1     1     0     Use external clock, falling edge
        //   1     1     1     Use external clock, rising edge

        switch (PRESCALING) {
        case 1:
                TCCR1B |=  (1 << CS10);
                TCCR1B &= ~(1 << CS11);
                TCCR1B &= ~(1 << CS12);
                break;
        case 8:
                TCCR1B &=  ~(1 << CS10);
                TCCR1B |= (1 << CS11);
                TCCR1B &= ~(1 << CS12);
                break;
        }
        
        uint16_t compare_value = F_CPU / PRESCALING / FREQUENCY_STEPPER - 1;
        
        /* Set the compare value: 
           
           F_STEPPER = 25000 (25 kHz)
           P_STEPPER = 1/25000 = 40 µs
           F_CPU = 16 MHz
           Prescaling = 1
           F_CLOCK = 16 MHz
           P_CLOCK = 1/16 µs
           N = 40 µs / (1/16 µs) = 640
           N-1 = 639

           F_STEPPER = 10000 (10 kHz)
           P_STEPPER = 1/10000 = 100 µs
           F_CPU = 16 MHz
           Prescaling = 8
           F_CLOCK = 16 MHz / 8 = 2 MHz
           P_CLOCK = 1/2 µs
           N = 100 µs / (1/2 µs) = 200
           N-1 = 199

           int n = (1 / F_STEPPER) / (1 / F_CPU / prescaling) - 1
                 = F_CPU / (F_STEPPER * prescaling) - 1
                 = 639
         */
        OCR1A = compare_value;
        // Serial.print("stepper.c: compare_value=");
        // Serial.println(compare_value);
}

/**
 * \brief The interrupt service handler for the reset-step-pins timer
 */
ISR(TIMER2_COMPA_vect)
{
        reset_step_pins();
        disable_reset_step_pins_timer();
        //counter_reset_timer++;
}

/**
 * \brief The interrupt service routine for the stepper timer.
 *
 */
ISR(TIMER1_COMPA_vect)
{
        /* If a reset is requested, set the current block and other
         * state variables to zero and return. */
        if (stepper_reset_) {
                current_block_ = 0;
                interrupts_ = 0;
                milliseconds_ = 0;
                stepper_reset_ = 0;
                return;
        }

        /* If there is no block active then pop the next block from
         * the buffer and do some initialization.  */
        if (current_block_ == 0) {
                
                current_block_ = block_buffer_get_next();

                if (current_block_ == 0) {
                        return;
                }
                
                /* Do the necessary initializations for the new
                 * block. */
                
                interrupts_ = 0;
                milliseconds_ = 0;
                
                if (current_block_->type == BLOCK_MOVE
                    || current_block_->type == BLOCK_MOVETO
                    || current_block_->type == BLOCK_MOVEAT) {

                        /* Sanity check */
                        if (current_block_->type == BLOCK_MOVE
                            && current_block_->data[DT] <= 0) {
                                        current_block_ = 0;
                                        return;
                        }
                        
                        /* Check the direction and set DIR pins. */
                        uint8_t dir = 0;
                        step_dir_[0] = 1;
                        step_dir_[1] = 1;
                        step_dir_[2] = 1;
                        
                        delta_[0] = (int32_t) current_block_->data[DX];
                        delta_[1] = (int32_t) current_block_->data[DY];
                        delta_[2] = (int32_t) current_block_->data[DZ];

                        /* For moveto events, substract the current
                         * position of the CNC. */
                        if (current_block_->type == BLOCK_MOVETO) {
                                // if (delta_[0] < 0)
                                //         delta_[0] = 0;
                                // else
                                        delta_[0] -= stepper_position_[0];
                                
                                // if (delta_[1] < 0)
                                //         delta_[1] = 0;
                                // else
                                        delta_[1] -= stepper_position_[1];
                                
                                // if (delta_[2] < 0)
                                //         delta_[2] = 0;
                                // else
                                        delta_[2] -= stepper_position_[2];
                        }

                        /* Check the directions */
                        if (delta_[0] < 0) {
                                toggle_dir(dir, X_DIRECTION_BIT);
                                delta_[0] = -delta_[0];
                                step_dir_[0] = -1;
                        }
                        if (delta_[1] < 0) {
                                toggle_dir(dir, Y_DIRECTION_BIT);
                                delta_[1] = -delta_[1];
                                step_dir_[1] = -1;
                        }
                        if (delta_[2] < 0) {
                                toggle_dir(dir, Z_DIRECTION_BIT);
                                delta_[2] = -delta_[2];
                                step_dir_[2] = -1;
                        }

                        /* Set the direction output pins */
                        set_dir_pins(dir);
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

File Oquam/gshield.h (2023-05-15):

/*
  romi-rover

  Copyright (C) 2019 Sony Computer Science Laboratories
  Author(s) Peter Hanappe

  romi-rover is collection of applications for the Romi Rover.

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
  You should have received a copy of the GNU General Public License
  along with this program.  If not, see
  <http://www.gnu.org/licenses/>.

 */
#include <avr/io.h>
#include <avr/interrupt.h>

#ifndef _OQUAM_GSHIELD_H_
#define _OQUAM_GSHIELD_H_

#define ENABLE_PIN_HIGH   0
#define ENCODER_REVERSED 0
/* #define PRESCALING         1 */
/* #define FREQUENCY_STEPPER  25000 */
/* #define INTERRUPTS_PER_MILLISECOND 25 */
#define PRESCALING         8
#define FREQUENCY_STEPPER  10000
#define INTERRUPTS_PER_MILLISECOND 10

#define PIN_LIMIT_SWITCH_X   9
#define PIN_LIMIT_SWITCH_Y   10
#define PIN_LIMIT_SWITCH_Z   11
#define PIN_SPINLDE          12

/* 
 * The STEP_ and DIRECTION_ defines below are taken from Grbl.
 */

/** 
 * Define step pulse output pins. NOTE: All step bit pins must be on
 * the same port. 
 */
#define STEP_DDR          DDRD
#define STEP_PORT         PORTD
#define X_STEP_BIT        2  // Uno Digital Pin 2
#define Y_STEP_BIT        3  // Uno Digital Pin 3
#define Z_STEP_BIT        4  // Uno Digital Pin 4
#define STEP_MASK         ((1 << X_STEP_BIT) | (1 << Y_STEP_BIT) | (1 << Z_STEP_BIT))

/** 
 * Define step direction output pins. NOTE: All direction pins must be
 * on the same port.
 */
#define DIRECTION_DDR     DDRD
#define DIRECTION_PORT    PORTD
#define X_DIRECTION_BIT   5  // Uno Digital Pin 5
#define Y_DIRECTION_BIT   6  // Uno Digital Pin 6
#define Z_DIRECTION_BIT   7  // Uno Digital Pin 7
#define DIRECTION_MASK    ((1<<X_DIRECTION_BIT)|(1<<Y_DIRECTION_BIT)|(1<<Z_DIRECTION_BIT))

/**
 * Define stepper driver enable/disable output pin.
 */
#define STEPPERS_DISABLE_DDR    DDRB
#define STEPPERS_DISABLE_PORT   PORTB
#define STEPPERS_DISABLE_BIT    0  // Uno Digital Pin 8
#define STEPPERS_DISABLE_MASK   (1 << STEPPERS_DISABLE_BIT)

/**
 * \brief Configure the step and dir pins as output.
 */
void init_pins();

/**
 * \brief Raise the enable pin.
 */
#define set_enable_pin_high()                                               \
        {                                                               \
                STEPPERS_DISABLE_PORT |= (1 << STEPPERS_DISABLE_BIT);   \
        }

/**
 * \brief Reset the enable pin.
 */
#define set_enable_pin_low()                                            \
        {                                                               \
                STEPPERS_DISABLE_PORT &= ~(1 << STEPPERS_DISABLE_BIT);  \
        }


/**
 * \brief Enable the step pins according to mask.
 */
#define set_step_pins(__mask)                           \
        {                                               \
                STEP_PORT |= __mask;                    \
        }

/**
 * \brief Reset the step pins to zero.
 */
#define reset_step_pins()                               \
        {                                               \
                STEP_PORT &= ~STEP_MASK;                \
        }

/**
 * \brief Toggle a step bit in the pins mask.
 */
#define toggle_step(__mask, __axis)                     \
        {                                               \
                __mask |= (1 << __axis);                \
        }

#define toggle_x_step(__mask)  toggle_step(__mask, X_STEP_BIT)
#define toggle_y_step(__mask)  toggle_step(__mask, Y_STEP_BIT)
#define toggle_z_step(__mask)  toggle_step(__mask, Z_STEP_BIT)

/**
 * \brief Enable the DIR pins according to mask.
 */
#define set_dir_pins(__pins)                            \
        {                                               \
                DIRECTION_PORT &= ~DIRECTION_MASK;      \
                DIRECTION_PORT |= __pins;               \
        }
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

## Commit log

2021-07-23 materials table
2021-08-26 Revisions with Peter
    [large_button.FCStd]
2023-04-24 added autofocus module
    [FocusMicroscope.scad, LinearSlider.dxf, LinearSlider.scad, SampleHolderRail.dxf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]
2023-04-27 rename Z
    [FocusMicroscope.scad, FrontPanel.stl, LinearSlider.dxf, LinearSlider.scad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]
2023-12-08 coarse control piezo thorlabs
    [z_focus_55_teeth_190.stl]
2023-12-08 Update Z stage
2023-12-08 Update Z-stage bis

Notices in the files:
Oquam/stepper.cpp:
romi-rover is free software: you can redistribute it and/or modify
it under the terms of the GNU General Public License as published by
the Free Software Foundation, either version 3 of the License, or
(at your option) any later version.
